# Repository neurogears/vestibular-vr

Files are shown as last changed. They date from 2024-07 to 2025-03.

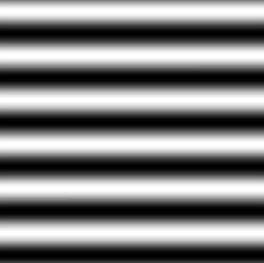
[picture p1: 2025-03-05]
Textures/horGrat.jpg

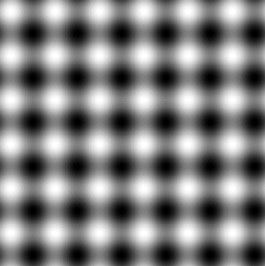
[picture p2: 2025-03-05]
Textures/plaid.jpg

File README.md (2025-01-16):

# vestibular-vr
Closed-loop VR setup for Rancz Lab

[Design Document](https://github.com/neurogears/vestibular-vr/blob/main/Design%20Documents/Vestibular%20VR%20Design%20Document.md)

### Acquisition Prerequisites

The following need to be installed on a fresh system in order to bootstrap the Bonsai environment correctly:

* Windows 10 or greater
* [Visual Studio Code](https://code.visualstudio.com/) (recommended for editing code scripts and git commits)
* [.NET 8.0 SDK](https://dotnet.microsoft.com/en-us/download/dotnet/8.0)
* [.NET Framework 4.7.2 Developer Pack](https://dotnet.microsoft.com/download/dotnet-framework/thank-you/net472-developer-pack-offline-installer) (required for intellisense when editing code scripts)
* [Git for Windows](https://gitforwindows.org/) (recommended for cloning and manipulating this repository)
* [Visual C++ Redistributable for Visual Studio 2012](https://www.microsoft.com/en-us/download/details.aspx?id=30679) (native dependency for OpenCV)
* [FTDI CDM Driver 2.12.28](https://www.ftdichip.com/Drivers/CDM/CDM21228_Setup.zip) (serial port drivers for HARP devices)
* [Spinnaker SDK 1.29.0.5](https://www.flir.co.uk/support/products/spinnaker-sdk/#Downloads) (device drivers for FLIR cameras, sign in required, look in the archived stable versions for 1.29.0.5)

### Setting up the Bonsai environment

To set up a Bonsai environment for running vestibular-vr, use the terminal to clone the repo into a local folder:

``` 
git clone https://github.com/neurogears/vestibular-vr.git
```

Now navigate into vestibular-vr/bonsai folder and run the `Setup.ps1` script (on Windows right-click > Run with powershell). Once all dependencies have been restored Bonsai can be launched in a local environment from the `.exe` in this folder.

### Session settings

Experiment parameters are based on a json schema (`schema.json` in the repo). Implementations of this schema are defined in `.yml` files provided by the user that are then loaded in the main Bonsai workflow to set up experiment parameters.

#### Working with schemas in Visual Studio Code
To create and edit schema implementations with full autcomplete and hinting, Visual Studio Code requires some extensions to be added:
* json (ZainChen.json)
* JSON Schema Validator (tberman.json-schema-validator)
* YAML (redhat.vscode-yaml)

#### Creating an experiment parameter file
To create an experiment parameter file based on the `schema`, create a new `.yml` file and add a reference to the `schema` at the top of the file

```
%YAML 1.1
---
# yaml-language-server: $schema=schema.json
```

The `schema` has two main groups of properties that define global experiment parameters, and block-specific parameters respectively, e.g.:

```
metadata:
  animalId: plimbo
  rootPath: D:/TrialLogicTestData/
  runGain: 0.0005

blocks: [
  &blockA
  {
    stimulus: {type: "grating"},
    totalRuntime: 20,
    runThreshold: 100,
    decayTimestep: 0.1,
    runThresholdDecay: -1,
    haltProbability: 0.5,
    haltProtocol: {
      minumumDelay: 0.1,
      randomDelay: 1.5,
      haltTime: 2,
      haltGain: 0
    }
  },
  &blockB
  {
    stimulus: {type: "cloud"},
    totalRuntime: 140,
    runThreshold: 200,
    decayTimestep: 0.1,
    runThresholdDecay: -1,
    haltProbability: 0.7,
    haltProtocol: {
      minumumDelay: 0.1,
      randomDelay: 0.5,
      haltTime: 0.5,
      haltGain: 0
    }
  },
  {<<: *blockA},
  {<<: *blockB}
]
```

The description of each parameter's effect on the Bonsai workflow, along with its type and default values are defined within `schema.json` itself. Note that where a parameter is not specifically set in the `.yml` the value will revert the default.

### Running an experiment
To run an experiment, run the Bonsai application from the local environment and open Main.bonsai. Use the property grid to select the desired experiment parameter `.yml` file.

### Python environment

The following need to be installed once on a fresh new system in order to analyze data:

 * [Visual Studio Code](https://code.visualstudio.com/) (recommended for editing code scripts and git commits)
 * A Conda distribution such as [Miniconda](https://docs.anaconda.com/free/miniconda/index.html)
 * [Python Extension for VS Code](https://marketplace.visualstudio.com/items?itemName=ms-python.python)
   * This extension needs to be made aware of the Conda installation. To do so, navigate to the extension settings. Under the section **Python: Conda Path**, enter the full path to the conda.bat executable. ([more info](https://stackoverflow.com/a/77615160/3312269).)
 * [Jupyter Extension for VS Code](https://marketplace.visualstudio.com/items?itemName=ms-toolsai.jupyter)

#### Create local Environment
1. Open the vestibular-vr folder in VS Code
2. `Ctrl+Shift+P` in VS Code > Python: Create Environment
   * Select Conda
   * Select Python 3.11 kernel
3. Ensure pip is upgraded:
 ```
 pip install --upgrade pip
 ```
4. From the terminal run `pip install -r requirements.txt`
5. Clone aeon_mecha into a separate directory 
 ```
 git clone https://github.com/SainsburyWellcomeCentre/aeon_mecha.git 
 ```
6. From the VS Code terminal, `cd` into the aeon_mecha directory and run:
 ```
 python -m pip install -e .
 ```

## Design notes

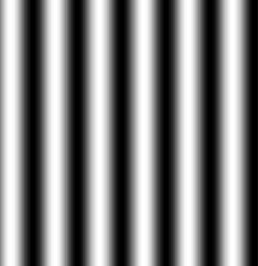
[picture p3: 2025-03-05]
Textures/vertGrat.jpg

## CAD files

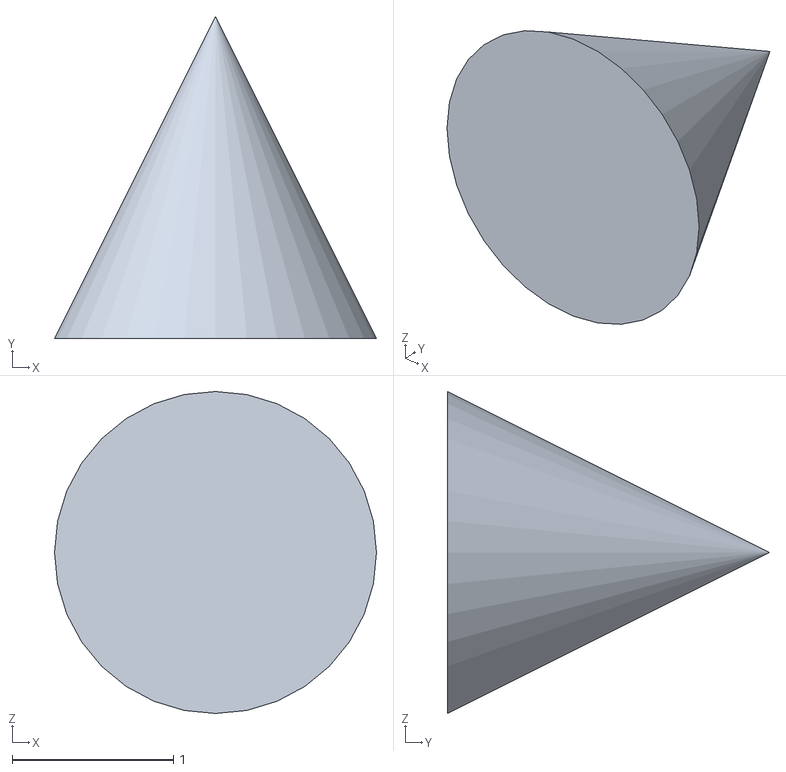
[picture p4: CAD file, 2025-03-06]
Models/cone.obj
2.00 x 2.00 x 2.00

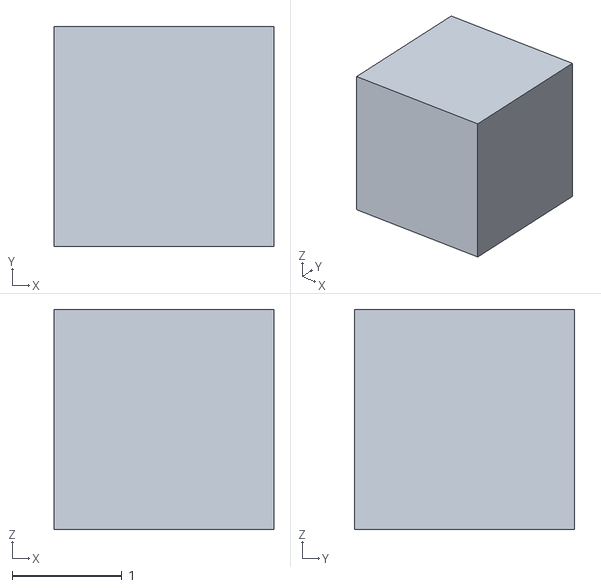
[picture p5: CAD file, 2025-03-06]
Models/box.obj
2.00 x 2.00 x 2.00

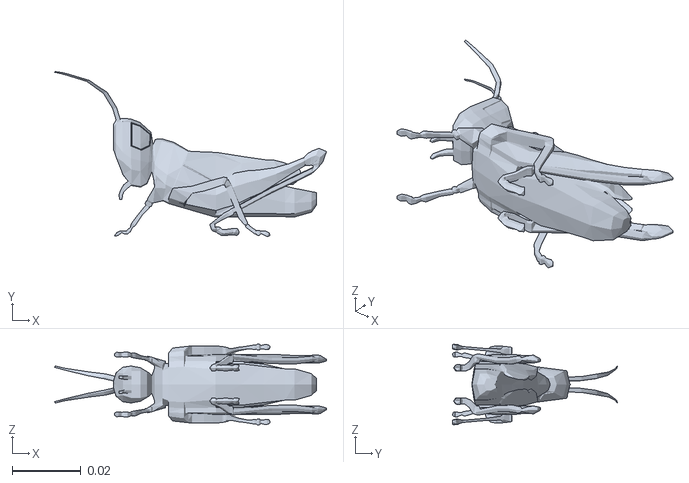
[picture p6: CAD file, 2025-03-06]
Models/cricket.obj
0.0788 x 0.0478 x 0.0234

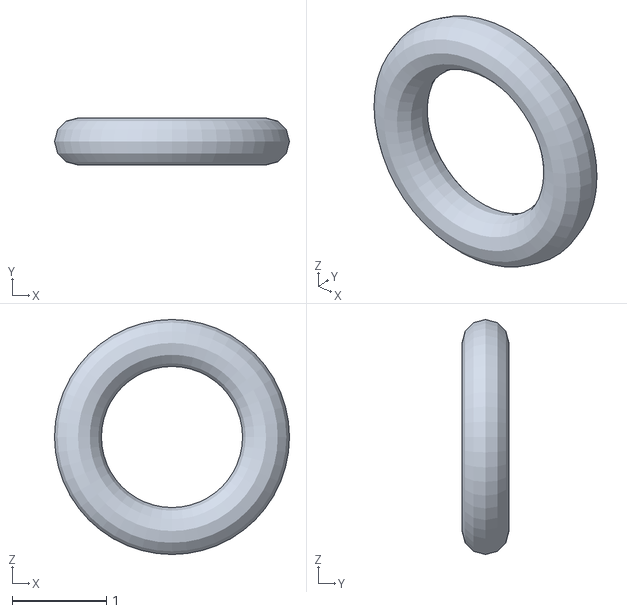
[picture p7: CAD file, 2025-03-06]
Models/torus.obj
2.50 x 0.5 x 2.50

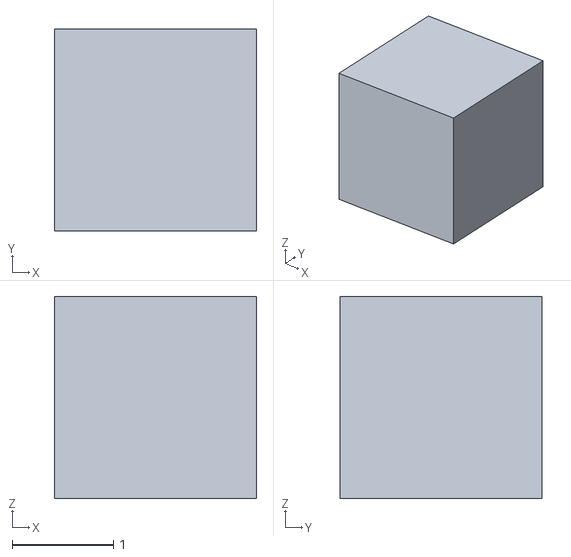
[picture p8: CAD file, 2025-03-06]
Models/cube.obj
2.00 x 2.00 x 2.00

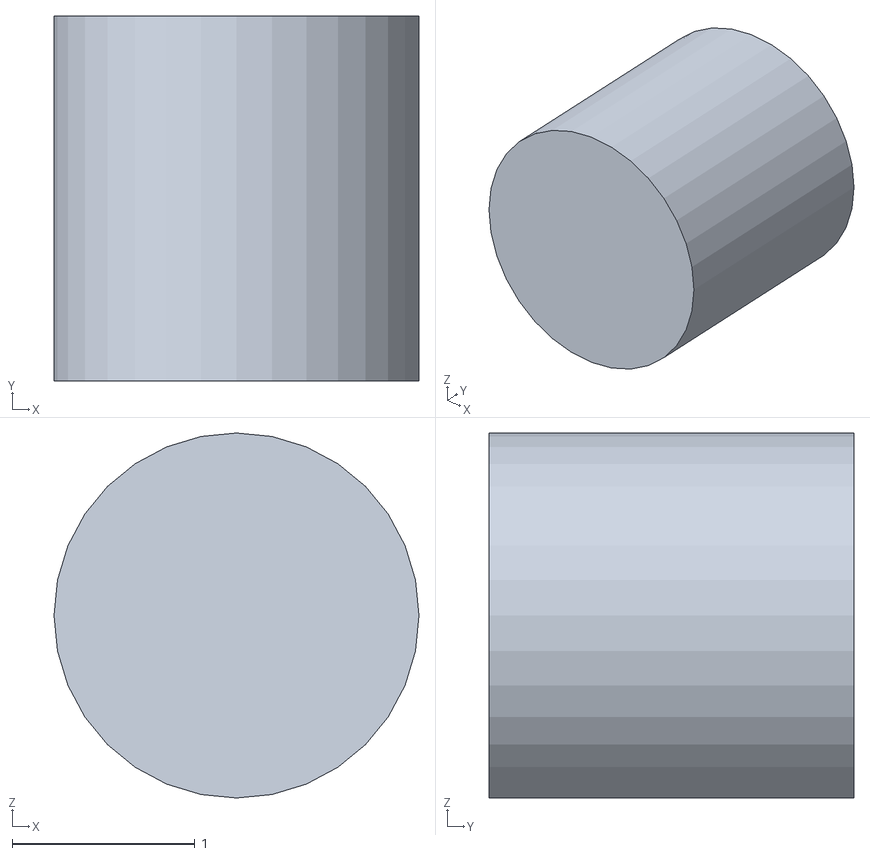
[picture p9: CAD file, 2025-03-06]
Models/cylinder.obj
2.00 x 2.00 x 2.00

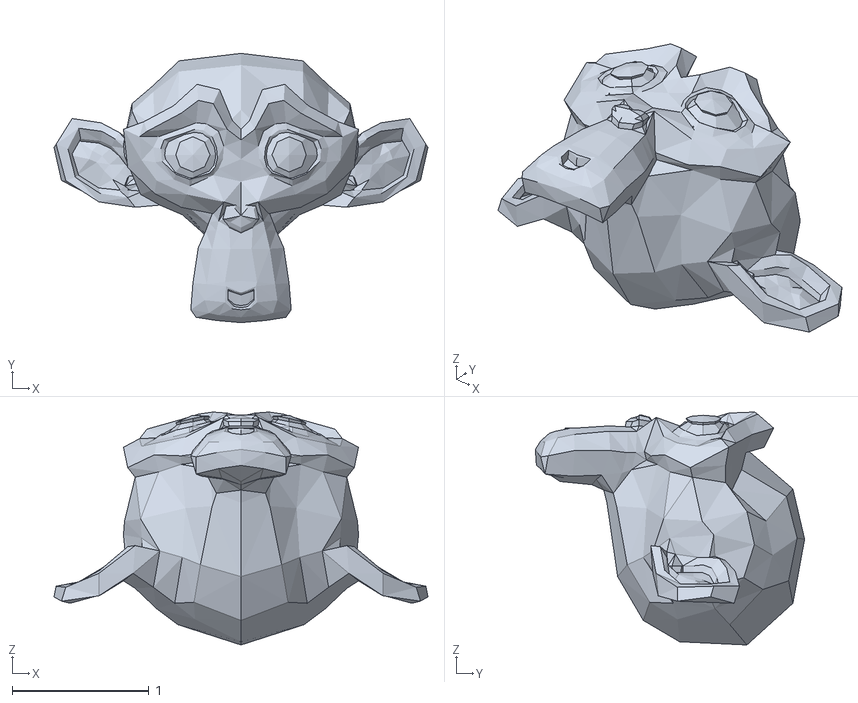
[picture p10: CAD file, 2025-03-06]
Models/suzanne.obj
2.73 x 1.97 x 1.70

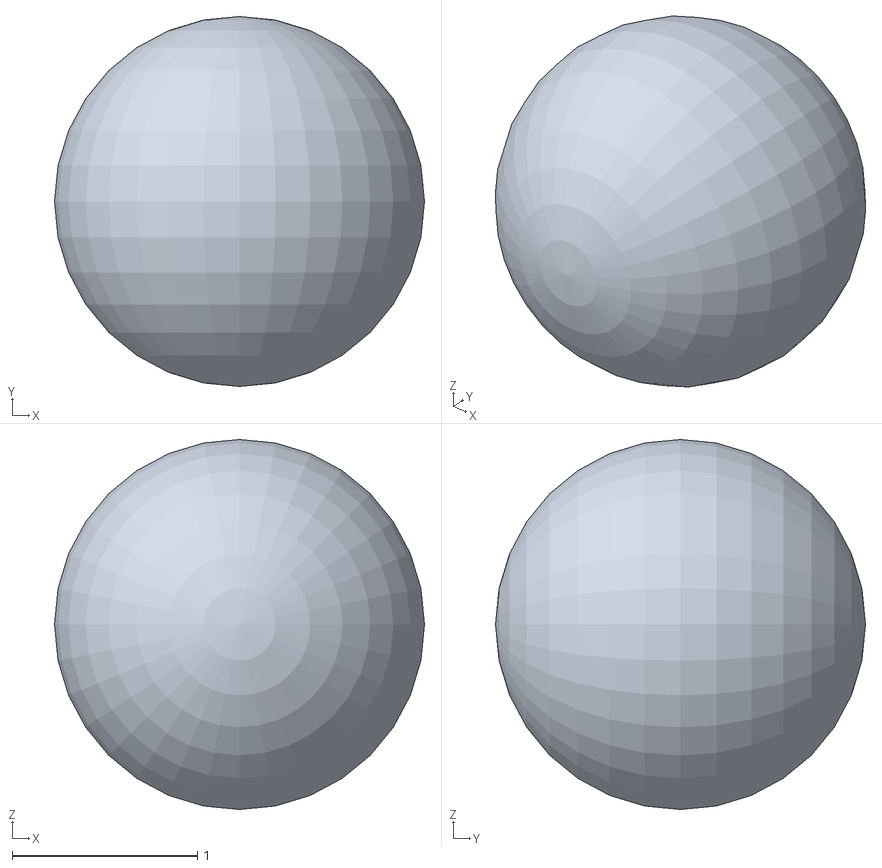
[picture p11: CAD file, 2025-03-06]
Models/sphere.obj
2.00 x 2.00 x 2.00

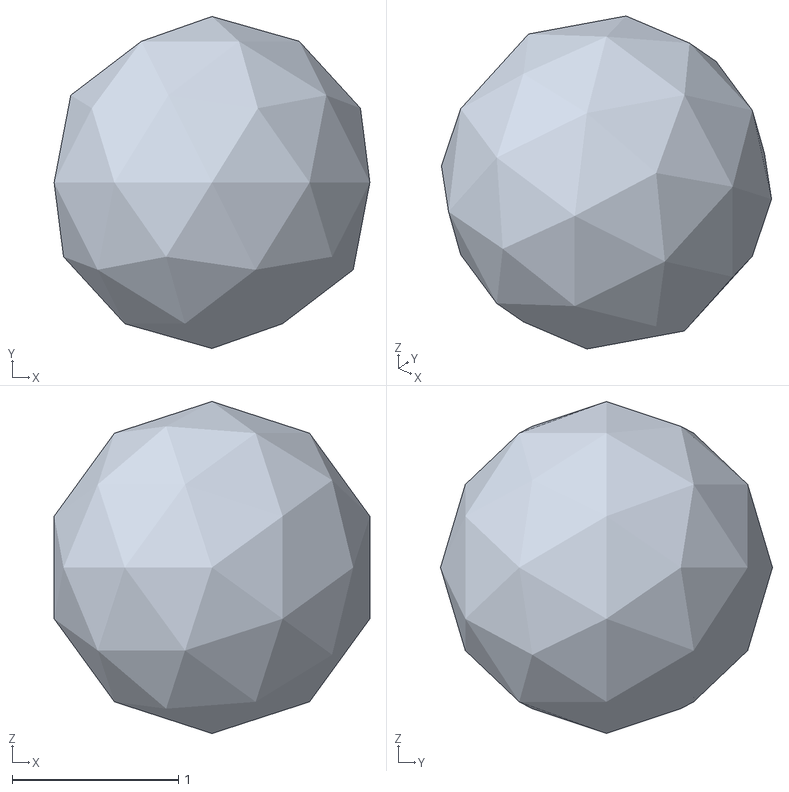
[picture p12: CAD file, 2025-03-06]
Models/icosphere.obj
1.90 x 2.00 x 2.00

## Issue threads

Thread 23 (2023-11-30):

### ISSUE TITLE
Video wall benchmarks

### ISSUE THREAD

**Issue by RoboDoig** [neurogears/vestibular-vr#23]
We need to test latency, jitter and synchronisation across screens with the matrox video wall.

- Thorlabs photodiodes
- Sampled through ONIX
- Standard closed-loop workflows for latency etc. timings
- NGR will provide workflow to be used onsite.

**Comment by ederancz** [comment]
Hey Andrew, can we close this or are you still analysing the data? Report the results here and then we can close it.

**Comment by RoboDoig** [comment]
Yes we should be able to soon, I'll upload the benchmark results here.

Do you have any kind of permanent cloud storage for lab data? Would be better to store raw data there rather than on the git repo.

**Comment by ederancz** [comment]
Good idea! 

We have a lab google drive, but I am not sure what is the easiest way for you to upload other than through the setup computer (Chrome should be logged in to ranczlab).

**Comment by RoboDoig** [comment]
Synchronisation between screens looks good, sub-millisecond

![image](https://github.com/neurogears/vestibular-vr/assets/11314305/0fb3f2a3-a3f0-4197-8a2b-1f748bbc637c)

**Comment by RoboDoig** [comment]
For latency and jitter, picture is a bit weirder. Hangs around 100ms latency. Jitter is mostly low but there are these higher latency events that pushes it up.

I would definitely expect these values to be lower, would be good to try this experiment again, also with a direct screen connection (not via Matrox) to compare.

![image](https://github.com/neurogears/vestibular-vr/assets/11314305/f0ffbe92-cf4f-452d-b734-81b19526971f)

**Comment by RoboDoig** [comment]
Poking around in the NVIDIA settings just now I also notice that there are a few options enabled that might slow down the display latency, let me know when available to repeat the test, I guess preferably after the rig has been moved.

**Comment by ederancz** [comment]
Cool, the setup won’t move before end of Jan, so Nora can set it up.-----------Sent from my phone, please excuse typos and brevity.On 22 Nov 2023, at 16:15, RoboDoig ***@***.***> wrote: 
Poking around in the NVIDIA settings just now I also notice that there are a few options enabled that might slow down the display latency, let me know when available to repeat the test, I guess preferably after the rig has been moved.

**Comment by RoboDoig** [comment]
Datasets for second round of benchmarks:

- Data2023_11_30_11_40_25 : Matrox only round-trip latency test
- Data2023_11_30_11_43_44: Matrox only screen-sync test

**Comment by RoboDoig** [comment]
Benchmarks with matrox only, NVIDIA ultra low latency mode, shader window focused on rig screens:

Screen_Sync:
![image](https://github.com/neurogears/vestibular-vr/assets/11314305/81edf5f5-a0cd-4a0f-84b4-765798e4cea6)

Round_Trip:
![image](https://github.com/neurogears/vestibular-vr/assets/11314305/873625fb-bb2d-49d1-ba2b-0f373cd7a06b)

I just noticed after doing this that the resolution set for the Matrox was at 7680x1080, at which the max refresh rate is 30Hz. Makes sense for the round-trip data where we are getting 1-2 frame delay at 30Hz. Will test at lower resolution with the full 60Hz, but will need someone to see what this physically looks like in the rig!

**Comment by RoboDoig** [comment]
Redid benchmarks with all monitors connected and latency jumped back up to ~100ms. @EleonoraAmbrad noticed that this was caused by Windows auto-selecting the Intel GPU as default when monitors are connected there. Fixed by forcing GPU choice to NVIDIA for the Bonsai exectuable in Windows graphics settings, Latency back down to 25-40ms.

**Comment by RoboDoig** [comment]
Added PR #34 which implements the benchmark workflows. I will merge the analysis scripts in a separate pull request, but closing this issue for now as desired latency / sync metrics achieved.

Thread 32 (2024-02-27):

### ISSUE TITLE
Implement full trial logic workflow

### ISSUE THREAD

**Issue by RoboDoig** [neurogears/vestibular-vr#32]
https://docs.google.com/document/d/1ItwPv-uNasmxrRA4Ncf8WAsi-0kBjkIqgoNdd-BLEN4/edit

**Comment by EleonoraAmbrad** [comment]
comments after meeting on the 7.11: trial logic works really well for our purposes, we would however like to control the time of the trials and not only the amount of halts / gain modulation episodes presented.

**Comment by RoboDoig** [comment]
Going back over this and I think I've been confusing myself with the concept of a 'trial' in this context.

Would it be fair to say that desired behaviour is to set for each block (e.g. mismatch block type 1)

- The total time the block should run for
- The minimum running threshold before a halt
- The probability of giving a halt after the threshold is reached
- The minimum delay before giving this halt if chosen, + a randomly sampled delay
- The total time the halt should be applied (contingent on the animal still running)
- The gain applied on each halt (e.g. 0 for total halt)

From re-reading the description it seems like there are not really discrete trials, just the process of checking running threshold and deciding whether to halt or not repeated throughout the block. I guess my question is whether any parameters need to change on each halt decision / presentation or whether these parameters are the same throughout the block (with the obvious exception of the random delay added to the minimum delay).

**Comment by EleonoraAmbrad** [comment]
yes, all you say here is correct, the parameters are set for each block. I think the word trial is a bit misleading, as each block will contain the set of parameters you listed and nothing should change except the random delay after the minimal delay

**Comment by RoboDoig** [comment]
Ok that's great thanks! I'm much clearer on this now.

**Comment by EleonoraAmbrad** [comment]
NPX data visualiser: following the meeting on the 2.2.24, we agreed with Gonçalo that the shader visualiser should be calibrated to our data.

In the Debug workflow, one of the NPX channels was streamed to the AnalogIO on the ONIX, then displayed on an oscilloscope. This works well on this workflow, but not in the "Insertion Workflow" that is used to record data at the moment (data displayed by the oscilloscope does not match voltage trace recorded by ONIX). 

It would be great if the changes applied in the MinimalONIXDebug workflow were replicated in the Insertion Workflow

**Comment by RoboDoig** [comment]
> NPX data visualiser: following the meeting on the 2.2.24, we agreed with Gonçalo that the shader visualiser should be calibrated to our data.
> 
> In the Debug workflow, one of the NPX channels was streamed to the AnalogIO on the ONIX, then displayed on an oscilloscope. This works well on this workflow, but not in the "Insertion Workflow" that is used to record data at the moment (data displayed by the oscilloscope does not match voltage trace recorded by ONIX).
> 
> It would be great if the changes applied in the MinimalONIXDebug workflow were replicated in the Insertion Workflow

This s added with PR #40

**Comment by RoboDoig** [comment]
Closing this issue with PR #44

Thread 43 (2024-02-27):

### ISSUE TITLE
ONIX failure after NewScale runtime error

### ISSUE THREAD

**Issue by RoboDoig** [neurogears/vestibular-vr#43]
The purpose of this issue for now is to keep a record of an observed bug.

Workflows containing the NstDevice operator can produce a runtime error if no NewScale device is connected. It seems that this error also interferes with initialisation of ONIX components by Bonsai and causes the ONIX device to end up in a weird state which crashes when the workflow is reset. The hardware can be reset by running the oni-repl program.

Can't really do anything about this until the ONIX Bonsai interface is updated. For now need to make sure NewScale is connected before starting any workflows with ONIX components.

**Comment by EleonoraAmbrad** [comment]
good idea to open this issue! 

could you remind me whether the liboni repo that you used was the one we had backed up from the previous computer or if you had to build the solution on visual code starting from the newly downloaded repo? I think I missed that yesterday. Thanks!

**Comment by RoboDoig** [comment]
In the end I did not use the backed up liboni folder. I cloned the repo and built the oni-repl.exe from source.

Closing this issue in favor of #45

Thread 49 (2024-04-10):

### ISSUE TITLE
Workflow specifications

### ISSUE THREAD

**Issue by RoboDoig** [neurogears/vestibular-vr#49]
@EleonoraAmbrad @ederancz Please use this issue to upload detailed specs for final experiment workflows.

**Comment by EleonoraAmbrad** [comment]
when using the workflow "TrialLogicTest" I ran into two behavior I did not understand:
- does the workflow stop after a few number of halts have been reached no matter the block length? This happened when setting halt probability to >0. Also, when this happens, the next commands are ignored (i.e. the blocks do not repeat even if specified in the json file)
- I am not sure the block gain modifier in the json file is working, the global gain seems to be the only one taken into account?

**Comment by RoboDoig** [comment]
> when using the workflow "TrialLogicTest" I ran into two behavior I did not understand:
> 
>     * does the workflow stop after a few number of halts have been reached no matter the block length? This happened when setting halt probability to >0. Also, when this happens, the next commands are ignored (i.e. the blocks do not repeat even if specified in the json file)
> 
>     * I am not sure the block gain modifier in the json file is working, the global gain seems to be the only one taken into account?

The workflow should not stop after a certain number of halts, the only thing that should stop the block is the block length timer if I recall correctly. Is it always stopping after a certain number of halts?
The block gain modifier is definitely implemented, it should multiply the global gain

**Comment by RoboDoig** [comment]
Some comments on the workflow specification that I'd like to clarify:

- "The rotation of the VR should be coupled to the motor movement..." - as I understand it we should therefore couple VR movement to the rotary encoder?
- Will playback just be playback of the visual stimulus, or the motor movement as well?
- "Motion cloud - link to python configuration script": To be clear, at the moment the motion clouds are generated via a python script as static texture sequences and loaded as a texture movie in Bonsai. Does this need to change? I think we had agreed that it was better to pre-generate the texture sequences rather than having them load dynamically.
- Algorithm 2 is greyed out in the experimental design document, is it required?

**Comment by EleonoraAmbrad** [comment]
> > when using the workflow "TrialLogicTest" I ran into two behavior I did not understand:
> > ```
> > * does the workflow stop after a few number of halts have been reached no matter the block length? This happened when setting halt probability to >0. Also, when this happens, the next commands are ignored (i.e. the blocks do not repeat even if specified in the json file)
> > 
> > * I am not sure the block gain modifier in the json file is working, the global gain seems to be the only one taken into account?
> > ```
> 
> The workflow should not stop after a certain number of halts, the only thing that should stop the block is the block length timer if I recall correctly. Is it always stopping after a certain number of halts? The block gain modifier is definitely implemented, it should multiply the global gain

I had the impression that the workflow stopped too early after setting halt probability to >0. For sure, the blocks that should come after do not start when this happens

**Comment by RoboDoig** [comment]
Could you send me an example SessionSettings file that produces this behavior? I will investigate

**Comment by EleonoraAmbrad** [comment]
> Some comments on the workflow specification that I'd like to clarify:
> 
> * "The rotation of the VR should be coupled to the motor movement..." - as I understand it we should therefore couple VR movement to the rotary encoder?

yes, that is what we thought. It would be analogous to reading out the PMW and translating it to VR motion, but for the rotation. 
> * Will playback just be playback of the visual stimulus, or the motor movement as well?

Just the VR. We would like to be able to control motor movement "freely" as well,  but that is a separate issue

> * "Motion cloud - link to python configuration script": To be clear, at the moment the motion clouds are generated via a python script as static texture sequences and loaded as a texture movie in Bonsai. Does this need to change? I think we had agreed that it was better to pre-generate the texture sequences rather than having them load dynamically.

no, this does not need to change, sorry, I formulated it wrong here. The way it'S working now is good!
> * Algorithm 2 is greyed out in the experimental design document, is it required?

no, it was a suggestion on how to implement the workflow, but does not necessarily need implementation
> 
> Finally, I think it would be ideal if we could combine both the linear flow and rotating drum environments into a single workflow. We could control the experiment type with block definitions as we do now.

this would be great, I think it would work well. Just to be clear, we would also like to display rotating visual stimuli passively and rotate the motor at a certain speed and gain (this should be mentioned in the new pdf, but I wanted to make sure it's clear again :D )

thanks a lot!

**Comment by RoboDoig** [comment]
Thanks @EleonoraAmbrad that makes things much clearer. Also as you say, the playback condition needs to still be implemented for both the linear and drum environments.

There is one distinction I still need to clarify: "It would be analogous to reading out the PMW and translating it to VR motion, but for the rotation." - 
We can link the VR movement to the PWM that is sent to the motor controller but ultimately this is calculated directly from the flow sensor reading. The alternative is that we read out the rotary encoder signal that is produced **as a result** of the motor movement and use that to drive the VR motion.

**Comment by RoboDoig** [comment]
I also have a question about the relationship between the four types of block. We have:

- Closed-loop
- Open-loop
- Mismatch
- Playback

As I understand it there are really only two conditions - closed-loop and open-loop. A mismatch block is always subset of a closed-loop block (where halt probaility > 0). A playback block is always a subset of an open-loop block. Is that correct?

**Comment by RoboDoig** [comment]
I think in fact all these conditions can be reduced to a single block type with different gain settings:

Linear, closed-loop:
- flow-->vr gain > 0 (or < 0)
- flow-->motor gain = 0
- rotary-->vr gain = 0
- playback-->vr gain = 0
- (+/-) mismatch parameters

Linear, playback:
- flow-->vr gain = 0
- flow-->motor gain = 0
- rotary-->vr gain = 0
- playback-->vr gain >0 (or <0)
- (+/-) mismatch parameters

Drum, closed-loop:
- flow-->vr gain = 0
- flow-->motor gain = >0 (or <0)
- rotary-->vr gain = >0 (or <0)
- playback-->vr gain = 0
- (+/-) mismatch parameters

Drum, playback:
- flow-->vr gain = 0
- flow-->motor gain = 0
- rotary-->vr gain = 0
- playback-->vr gain = >0 (or <0)
- (+/-) mismatch parameters

**Comment by RoboDoig** [comment]
Another couple of things to clarify:

"Rotation probability: probability of the played back or generated flow stopping at
each given time" - this suggests that there should be defined times for halting playback? Is this true or is it just with the randomisation parameters as implemented now?

**Comment by EleonoraAmbrad** [comment]
> I think in fact all these conditions can be reduced to a single block type with different gain settings:
> 
> Linear, closed-loop:
> 
> * flow-->vr gain > 0 (or < 0)
> * flow-->motor gain = 0
> * rotary-->vr gain = 0
> * playback-->vr gain = 0
> * (+/-) mismatch parameters
> 
> Linear, playback:
> 
> * flow-->vr gain = 0
> * flow-->motor gain = 0
> * rotary-->vr gain = 0
> * playback-->vr gain >0 (or <0)
> * (+/-) mismatch parameters
> 
> Drum, closed-loop:
> 
> * flow-->vr gain = 0
> * flow-->motor gain = >0 (or <0)
> * rotary-->vr gain = >0 (or <0)
> * playback-->vr gain = 0
> * (+/-) mismatch parameters
> 
> Drum, playback:
> 
> * flow-->vr gain = 0
> * flow-->motor gain = 0
> * rotary-->vr gain = 0
> * playback-->vr gain = >0 (or <0)
> * (+/-) mismatch parameters
> 
> This way you are also not as limited in choosing 1 of 4 block types. You can still construct the original types but also do things in between (e.g. have a drum playback block that also has some closed-loop rotary motion).

This looks really efficient and straightforward, I like it a lot. I can't see anything wrong with doing it this way. Basically one will control each component at the time.
How does one deal with length of the "block" though in this case? An extra parameter?

**Comment by EleonoraAmbrad** [comment]
> Thanks @EleonoraAmbrad that makes things much clearer. Also as you say, the playback condition needs to still be implemented for both the linear and drum environments.
> 
> There is one distinction I still need to clarify: "It would be analogous to reading out the PMW and translating it to VR motion, but for the rotation." - We can link the VR movement to the PWM that is sent to the motor controller but ultimately this is calculated directly from the flow sensor reading. The alternative is that we read out the rotary encoder signal that is produced **as a result** of the motor movement and use that to drive the VR motion.

This makes sense, it would be also more accurate I guess

**Comment by EleonoraAmbrad** [comment]
> Another thing to clarify:
> 
> "Rotation probability: probability of the played back or generated flow stopping at each given time" - this suggests that there should be defined times for halting playback? Is this true or is it just with the randomisation parameters as implemented now?

This I don't know about yet. Since we haven't finally implemented the playback I'm not sure anymore which strategy we had decided to go with (playback in VR of another mouses movement based on flow sensor or random generation of visual stimuli?) Both strategies are working I'd say, as long as the times when the halts occur are logged. I'm sorry if I'm not getting your question :/

**Comment by RoboDoig** [comment]
Re: playback - for now I am going to implement this with analog input as the source of the playback signal. This can be coupled to visual flow or motor movement in any way you want with the gain settings. Or you can change the source to be something other than analog input.

**Comment by RoboDoig** [comment]
Closing this issue as implemented and tested.

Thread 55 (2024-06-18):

### ISSUE TITLE
Provide example data files as reference

### ISSUE THREAD

**Issue by RoboDoig** [neurogears/vestibular-vr#55]
For working on some of the open issues (#53 #54) it would be beneficial to have some example logged data as a reference (in particular the HARP streams).

@EleonoraAmbrad could you provide some data from a run of the Main.bonsai trial logic workflow? This will be particularly useful as a reference for Filipe when implementing direct H1 --> H2 motor control.

**Comment by EleonoraAmbrad** [comment]
files sent via email (link to google drive folder)

**Comment by EleonoraAmbrad** [comment]
@RoboDoig asking for advice: I am looking at the data produced by the video writer node, the csv file VideoData1_1904-01-01T00-00-00.csv 
 It looks like there is some substantial frame loss over time? or am I interpreting things wrong? Do we need to reduce frame rate?

**Comment by EleonoraAmbrad** [comment]
> Hi @EleonoraAmbrad, what in the csv file is suggesting this? Is it just the number of frames or something in the frame timestamps?

Value.ChunkData.FrameID: these values are consecutive until a certain point (until frame 40), but then they are not anymore. Seems like every second frame is dropped after this, but it's not consistent (sometimes more or less than this)

**Comment by RoboDoig** [comment]
Also doesn't seem to be the case in the last dataset I downloaded from the google drive (2024-05-10T14-22-41). Are both cameras set at the same frame rate / exposure time?

**Comment by EleonoraAmbrad** [comment]
> Also doesn't seem to be the case in the last dataset I downloaded from the google drive (2024-05-10T14-22-41). Are both cameras set at the same frame rate / exposure time?

you're right, maybe there was a mistake then. Or maybe it's a problem when keeping the spin view software open? I need to do that to set the gain at the moment.

**Comment by EleonoraAmbrad** [comment]
on that specific file not, but if you look at VideoData1_1904-01-03T23-00-00.csv it happens there as well. 

Yeah the cameras have the same frame rate and exp time, but in general this shouldn't be a problem right? (they are on different triggers now). One thing that comes to mind is that I have to keep SpinView software open to set the gain, could that be an issue?

**Comment by RoboDoig** [comment]
> on that specific file not, but if you look at VideoData1_1904-01-03T23-00-00.csv it happens there as well.

On which dataset?

> Yeah the cameras have the same frame rate and exp time, but in general this shouldn't be a problem right? (they are on different triggers now). One thing that comes to mind is that I have to keep SpinView software open to set the gain, could that be an issue?

Keeping the software open shouldn't be an issue. 

Can you reproduce the missing frames reliably? If so what happens if you swap the trigger lines for the cameras?

**Comment by EleonoraAmbrad** [comment]
> > on that specific file not, but if you look at VideoData1_1904-01-03T23-00-00.csv it happens there as well.
> 
> On which dataset?
> 
> > Yeah the cameras have the same frame rate and exp time, but in general this shouldn't be a problem right? (they are on different triggers now). One thing that comes to mind is that I have to keep SpinView software open to set the gain, could that be an issue?
> 
> Keeping the software open shouldn't be an issue.
> 
> Can you reproduce the missing frames reliably? If so what happens if you swap the trigger lines for the cameras?

sorry, on the 2024-05-10T14-20-05. I don't think the loss can be reliably reproduced because these recordings were all done on the same day with the same settings, I only changed sampling rate and exp time. I am not sure whether this reliably happens with increasing sampling rate, for example, or when setting a sample rate that is too high for what the exposure time allows. In any case it's strange that this happens only for 1 camera when both had the same sampling rate and exposure time. I will test this more systematically, swap the triggers and come back to you asap

**Comment by EleonoraAmbrad** [comment]
I uploaded some more files in the drive. these files were acquired with harp clock sync device (received this week) connected to h2, and h2 sending clock signal to h1. 

in the last recorded files I see frame drops in both cameras even if I change the sampling rate and exposure time and swap the triggers. 

another interesting behavior is that sometimes when I stop the workflow and restart it, the cameras are already triggered. stopping the workflow and restarting it solves the issue. not a big deal I guess, unless it's indicative of underlying trigger issues?

**Comment by RoboDoig** [comment]
Hi @EleonoraAmbrad I'm closing this issue as the original problem is resolved. Could you create a new issue for the camera trigger observation if it's still a problem?

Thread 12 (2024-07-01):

### ISSUE TITLE
Bonsai workflows 

### ISSUE THREAD

**Issue by ederancz** [neurogears/vestibular-vr#12]
Hi @RoboDoig. There are 2 example workflows below. 

In general, all workflows should have the following: 
1. Some sort of lab-book / metadata (time/date, animal ID, various experiment parameters e.g. gain in open loop).
2. Save processed optical sensor signals as styrofoam ball position. If using 1 optical sensor, then cumulative forward travel of the animal (say in cm) and rotation (0-360 degrees). This will of course need to be calibrated. In the future, we may want to use 2 sensors and average them for the rotation measure. 
3. Trigger and save from 1 camera. In the future, online deepLabCut analysis would be sweet and perhaps only record pupil diameter and position. 
4. A homing function. Currently using a hall-effect sensor and a magnet and rotate the platform until we activate it. 

**Workflow 1. Closed loop** 
Inputs: Target position, speed, max acceleration 
Outputs: motor command, styrofoam ball position, video 
For the future: follow arbitrary waveform as a positional command 

**Workflow 2. Open loop** 
Inputs: optical sensor signal, gain (between optical sensor and motor movement)  
Outputs: motor command, styrofoam ball position, video

Regarding motor command, we should discuss motion control fairly soon. It is a big field, and I am not well-versed in it.

**Comment by RoboDoig** [comment]
Can I assume that this issue is superseded by #49 ? Is there anything mentioned in this issue that is missing from the more recent workflow specs?

**Comment by EleonoraAmbrad** [comment]
yes, this issue can be closed!

> Can I assume that this issue is superseded by #49 ? Is there anything mentioned in this issue that is missing from the more recent workflow specs?

I think we can close this issue, thank you !

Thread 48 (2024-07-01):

### ISSUE TITLE
Implement synchronisation between HARP and ONIX

### ISSUE THREAD

**Issue by RoboDoig** [neurogears/vestibular-vr#48]
Ideally, HARP interface of ONIX breakout will be used as a master clock for H1/H2.

Implement photodiode synchronisation on screens (flickering square to synchronise draw calls).

Use WithLatestTimestamp approach to log state changes in block state machine.

**Comment by EleonoraAmbrad** [comment]
we have a jack "stereo" cable that we can use for the synchronisation as suggested above. 

According to the design files, the harp interface signal should be split between H1 and H2, is this correct? If so, should I strip the cable and use the screw terminals on H1 and H2? 
![SignalRoutingDesign](https://github.com/neurogears/vestibular-vr/assets/143619542/50209ff6-1a8f-4c80-a445-6bba61ee1231)
![photo_2024-04-16 14 27 59](https://github.com/neurogears/vestibular-vr/assets/143619542/ac11d373-d42b-47cc-b2f1-f10b813ec53e)

**Comment by RoboDoig** [comment]
There are a couple of ways to do it, as you say you can take a stereo 3.5mm cable and have one end in H2, then bare wire in the screw terminals for H1. 

You can also get the HARP synchronizer (https://www.cf-hw.org/open-source-tools/electronic-devices/clock-synchronizer) which can act as the master clock source and has multiple output channels that you can send to H1, H2 and ONIX

**Comment by EleonoraAmbrad** [comment]
> There are a couple of ways to do it, as you say you can take a stereo 3.5mm cable and have one end in H2, then bare wire in the screw terminals for H1.
> if we were to go with this solution, how would the ONIX receive the sync signals? i.e. which connection on the breakout board should be setup?

**Comment by RoboDoig** [comment]
I don't think the ONIX can generate a HARP clock, it would rather be H2 generating the master clock and then H1 and ONIX receiving that clock. But yes, the cable would have to be split out from H2 to go to H1 and ONIX, e.g. with a 3.5mm splitter.

https://www.amazon.co.uk/PENCILUPNOSE%C2%A9-HEADPHONE-SPLITTER-EXTENSION-MOTOROLA-BLACK/dp/B079GBP6CV/ref=asc_df_B079GBP6CV/?tag=googshopuk-21&linkCode=df0&hvadid=375419269630&hvpos=&hvnetw=g&hvrand=17305413413427148390&hvpone=&hvptwo=&hvqmt=&hvdev=c&hvdvcmdl=&hvlocint=&hvlocphy=9046001&hvtargid=pla-1013889856952&psc=1&mcid=d37b23cc42a13f0186f1f5c3478351d8&tag=&ref=&adgrpid=85278568708&hvpone=&hvptwo=&hvadid=375419269630&hvpos=&hvnetw=g&hvrand=17305413413427148390&hvqmt=&hvdev=c&hvdvcmdl=&hvlocint=&hvlocphy=9046001&hvtargid=pla-1013889856952

**Comment by EleonoraAmbrad** [comment]
update after meeting with @RoboDoig : signal should not be split between H1 and ONIX from H2, so we will instead send a randomized synchronisation ANALOG output signal to H2 and ONIX. Analog output will be generated in bonsai. 

Ideally, in the future we should rely on https://www.cf-hw.org/open-source-tools/electronic-devices/clock-synchronizer to split clock output to H2 and ONIX, especially because H2 analog input may be needed for playback signal.

**Comment by RoboDoig** [comment]
After last week's discussion: to synchronize everything correctly it will definitely be necessary to use a clock-synchronizer. The H2 analog input is occupied by the hall sensor so it can't be used as a synchronisation signal. Solution will be to have the clock-sync connected to H2 and ONIX. H2 will then pass its clock signal to H1 via the rotary joint.

**Comment by EleonoraAmbrad** [comment]
Order for the clock synchroniser will be placed this week, lead time should be 2 days.

**Comment by EleonoraAmbrad** [comment]
quick question: the HARP sync signal sent to ONIX will go in the dedicated hair sync 3.5 mm connection? this means that we would need a cable with two male audio connectors (one for the jack on clock sync and one for the ONIX?)

**Comment by ederancz** [comment]
Implemented now. There is now way to test it (would need two identical HARP devices with the same inputs), but we have no reason to believe it is not working.

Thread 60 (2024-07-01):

### ISSUE TITLE
Array names in device schema for postprocessing

### ISSUE THREAD

**Issue by RoboDoig** [neurogears/vestibular-vr#60]
Currently, the device schema for H1 does not have names for array columns in e.g. OpticalTrackingRead. This causes an issue with postprocessing analysis as harp-python cannot parse the array data without modifications.

To fix this on the postprocessing branch, the device schema should use named columns for array data.

**Comment by RoboDoig** [comment]
@EleonoraAmbrad @ikharitonov I've made the changes to the analysis code we talked about in the meeting today. Try out the `reader-proto` branch for an example

**Comment by ikharitonov** [comment]
@RoboDoig thanks! OpticalTrackingRead works, along with Cam0Event, Cam1Event and StartAndStop, but the rest are failing with "ValueError: No objects to concatenate". Also we found the YAML file for H2 (https://github.com/harp-tech/device.vestibularH2/blob/main/Firmware/VestibularVrH2/device.yml), but most registers there are also failing to be read

**Comment by RoboDoig** [comment]
That might be because no events were logged for the other registers, for example if I look in the example harp data folder I have - I see events only for 32, 33, 38, 46 (Cam0Event, Cam1Event, StartAndStop, OpticalTrackingRead).

Could you double check whether reading a register fails even when there is definitely binary data available for it?

**Comment by ikharitonov** [comment]
You are right sorry, we realised after posting, readable registers match with available binaries

**Comment by RoboDoig** [comment]
Can you confirm it's working now? If so I will make a PR and close this issue.

**Comment by ederancz** [comment]
Working fine, device.yml files need updating (or confirming) for current firmware versions for H1 and H2, created issues at harp repos.

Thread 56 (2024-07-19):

### ISSUE TITLE
synchronisation of bonsai H1 and H2 events with photometery system

### ISSUE THREAD

**Issue by EleonoraAmbrad** [neurogears/vestibular-vr#56]
we would like to implement synchronisation between the data acquired via H1 and H2 and a photometry setup when using the Main experiment workflow.

https://www.rwdstco.com/product-item/dual-color-fiber-photometry-system/?_gl=1*r9q6pp*_up*MQ..*_ga*MTc5NzE1ODA1MS4xNzE1Nzc1MzE0*_ga_2P56W6VQP2*MTcxNTc3NTMxMy4xLjEuMTcxNTc3NTMzMi4wLjAuMA..&gclid=CjwKCAjwupGyBhBBEiwA0UcqaBYzOFXJ-Fceqbl8VPrT6yq4bXvHe9BTilrouICISsTUCkpdJtkFxxoCX_MQAvD_BwE (link to setup)

at the moment, a digital output of the ONIX is used to send a continuous 5V pulse to the RWD input to signal visual stimulus onset in a different workflow, but this approach is not optimal.

additionally, synchronisation with Harp devices would be required to align calcium imaging data to pupil tracking cameras and flow sensor data. Help with this would be greatly appreciated once we set up clock sync on H1 and H2!

**Comment by ederancz** [comment]
Requirements: 

1. Bonsai to generate pseudorandom TTL pulse and send it out of ONIX digital out. These need to be logged with HARP timestamps. 
2. This has to be implemented in a duplicate insertion.workflow to contain an ONI node.

**Comment by RoboDoig** [comment]
This all makes sense, just wondering about point 2. though - is there an advantage to using a premade csv file for the ON/OFF states vs. generating them online and logging the order for each experiment?

**Comment by EleonoraAmbrad** [comment]
we were maybe thinking it's easier, but if not then generating online is also an option of course

**Comment by RoboDoig** [comment]
My thinking is along these lines:

If you have a predetermined ON/OFF timing sequence loaded from .csv you have to load it into the workflow at runtime, which is fine. There may be a situation where you generate a few different .csv files for this, and you need to log somewhere which one you have used in Bonsai. This can be as simple as logging the name of the .csv file used, or you could 'relog' the entire file along with everything else to be 100% sure which sequence you used for synchronisation.

I can imagine a tricky situation happening somewhere down the line where you have been using a sequence file ('sequence.csv') and then at some point it's decided to change the sequence for some reason. The name of the logged file is the same but the sequence is different leading to potential confusion in later analysis.

This needs to be avoided, so to be safe we need to log the entire sequence anyway along with the corresponding HARP timestamps. Since this all needs to be logged anyway, to me it makes sense to just generate the sequence online in Bonsai. Unless there is some advantage of a predetermined sequence that I'm missing. Additionally, you can effectively have a predetermined sequence while generating it online by setting a seed for your random generator in the workflow.

**Comment by RoboDoig** [comment]
I've implemented a photometry sync signal in the photometry-sync branch. The signal is set on digital output 0 of the ONIX. To fully test we need to route that signal to the photometry setup and also reroute it to a digital input on the ONIX so we can ensure that it's being logged correctly with HARP timestamps.

**Comment by EleonoraAmbrad** [comment]
the photometry sync signal works well! as discussed, we would need the signal to stop right after the trial logic is over, to signal that the experiment is also finished (at the moment the TTL is still ON after the trial logic ends).

**Comment by RoboDoig** [comment]
I branched the digitalOUT from pin 0 to the A1 pin on ONIX

**Comment by EleonoraAmbrad** [comment]
i branched out the digitalO0 to A1 on onix

**Comment by RoboDoig** [comment]
I would suggest branching instead to a digital input line, the reason being that each digital input event is HARP timestamped, whereas the analog data is acquired and timestamped in chunks. Practically this might not make that much difference to your synchronisation precision, but if you ever e.g. change the chunk size of the analog inputs it might have an effect.

**Comment by RoboDoig** [comment]
Depending on the ONIX board you have, there is an issue with the HARP clock physical input. For certain versions of the ONIX board (I think this is an issue with 1.5B) the HARP clock jack actually sends a HARP clock signal OUT rather than receives the clock from an external device. Our design for the system relies on the ONIX board receiving the HARP clock from an external device.

My understanding is that they originally intended the ONIX boards to act as master HARP clocks sending clock signals out to other devices and then changed the direction in later versions.

To fix this at a hardware level, there is an adapter developed at OEPS that allows the ONIX board to receive HARP clock signals as input. I am asking Filipe how to obtain this. For now since the digital inputs of the ONIX are paired with HARP timestamps in the Bonsai workflow I suggest that we add another digital output --> digital input loopback in ONIX that can be used to synchronise HARP with the ONIX.

Potential solutions summarised:

1. Get a HARP clock adapter for ONIX from Filipe
2. Create another DO --> DI loopback in ONIX so that we can use DI events to synchronise with HARP
3. Depending on whether the photometry system is capable of recording at a high enough sampling rate, just speed up the photometry sync signal (rather than going for option 2)
4. Investigate whether the clock synchroniser device can be used as a repeater for the ONIX clock output.

Also please double check what version of the ONIX breakout board you have so we can confirm this is an issue that needs to be addressed.

**Comment by EleonoraAmbrad** [comment]
can confirm hat the board is the 1.5 B (beta). 

I am currently setting up the DO1->DI1 connection for the synchronistation and the DO0->DI0 for the photometry sync signal.
We cannot use the photometry sync signal for both purposes (option 3) because the analog IN is going to be sampled at rates between 10 and 30 Hz., so we should either revert the direction of the clock synchroniser device or use the digital loop while we wait for the adaptor.

**Comment by EleonoraAmbrad** [comment]
done

**Comment by RoboDoig** [comment]
Re: the sync signal stopping after trial logic is done. I assume by this you mean you want the sync signal to stop only after all blocks are done?

I'm not sure I understand why this is desirable as it creates some ambiguity when used as a trial logic signal as well as a photometry sync signal.

Consider the last block of the sequence, as the sync signal is switching high to low with a random time interval, if the last sync signal is a switch to low, followed by setting again at low for the end of the block sequence you would not know when the block had actually ended.

**Comment by RoboDoig** [comment]
Should be fixed by #64, pending testing.

**Comment by RoboDoig** [comment]
Confirmed working after testing.

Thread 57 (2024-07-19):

### ISSUE TITLE
Screen sync quad

### ISSUE THREAD

**Issue by RoboDoig** [neurogears/vestibular-vr#57]
Need to implement a method of synchronising screen updates, as well as visual halts with everything else (HARP ONIX)

Proposed solution is to use a flickering quad somewhere in the corner of the screen with a photodiode recording. The parameters of this flicker (e.g. color) should be changed during halt periods so we can recover both the screen update as well as the timing of each halt.

**Comment by ederancz** [comment]
## There are 2 subtasks. 

### A. the recording the photodiode signal via ONIX analogue input.
1kHz sampling rate should be enough (but we should test in action) 

### B. to signal the stimulus parameter. 
In one small square at the bottom of one of the screens via bonvision. 
We need 3 states as follows:
1. Idle (no vis stimulus) - middle grey 
2. Moving stimulus on (both open- and closed-loop modes) - white
3. Halt - black

**Comment by RoboDoig** [comment]
Regarding A) - this should be taken care of by the existing insertion workflow. We can't connect to the same ONIX board on the main workflow while the insertion workflow is running. I think this should already be essentially implemented since the insertion workflow is logging analogue data and is synchronised with HARP.

**Comment by EleonoraAmbrad** [comment]
@RoboDoig you are right, however, as we will not only use Main workflow with Insertion Workflow but also with the photometry setup, we could add an analog IO node in Main as well. We anyway need to create another one for the photometry to implement synchronisation signal (https://github.com/neurogears/vestibular-vr/issues/56).

**Comment by RoboDoig** [comment]
OK I see, so in the photometry version of the experiment, everything is contained in the Main workflow? No second insertion workflow running?

I've made a PR that should produce the desired screen behavior for recording with the photodiode. It should be possible to inspect that this works visually - see PR #62

**Comment by EleonoraAmbrad** [comment]
I tested the workflow, here are some of my remarks:

- I can position the quad in a good place for the photodiode to detect it, so that's good! The quad is mirrored on the neighbouring screen due to the VR mapping, but it shouldn't be a big deal.

- the halts are applied correctly when setting a halt probability >0 in the yml, but the quad does not change colour upon halt. Before TrialLogic start, the quad is grey (as displayed by the bonsai visualiser values). When the TrialLogic starts (using shift + space), the quad turns white. However, when a halt is applied to the VR, the quad does not change colour. This happens in both DrumClosedLoop and in LinearClosedLoop block

- I could not record the signal of the photodiode because there is no analogIN node yet, but I wasn't sure if that's on purpose (when using Main in combination with InsertionWorkflow in the future, I guess we can record the quad signal using the analog node already present in that workflow, as you suggested)

**Comment by RoboDoig** [comment]
Hi @EleonoraAmbrad, thanks for your feedback!

I will look into the colour not changing on halt, if the colour is changing for the other conditions it probably just means I forgot to update the colour switch somewhere in the halt condition, or assigned the wrong colour.

I didn't implement the ONIX stuff in this PR yet, this will be added in the photometry sync PR which I am working on finishing today. For now it can be recorded with a separate workflow if needed.

**Comment by RoboDoig** [comment]
I've updated the PR, the event that updated the halt color was indeed in the wrong place, should be working now!

**Comment by EleonoraAmbrad** [comment]
the quad changes colour as expected! I think it works perfectly well. 

One small comment: because the start of the logging and the start of the trial logic are controlled via two different key down combinations, and can therefore never be precise enough, we will use the change in colour from grey to white to indicate trial logic start and white to grey to indicate trial logic end. I don't think there should be any problem doing this, right?

PS I also did not record the analog signal yet, I wasn't sure if it is implemented in this PR.

**Comment by RoboDoig** [comment]
Closed with #67

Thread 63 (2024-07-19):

### ISSUE TITLE
H2 crash during recording 

### ISSUE THREAD

**Issue by ederancz** [neurogears/vestibular-vr#63]
On every block using the main workflow, H2 seems to crash after ~50 seconds. 
The minimal proportional control workflow does not have this issue. 
Below are a few notes from the logs. 

**H1 logs** for appropriate time (block length) + whenever logging was started and the workflow stopped 
**H2 logs** analogue input (39) and encoder (38) for only ~50 seconds (until the motor stops) 
	but 42 (pulse interval) is logged for the whole block 
	The platform can be rotated after this by hand (i.e. the motor is not clamped). 
	Closed loop visual stimulation keeps running for the block time. 
	There is an error message in the console (see 2 separate examples below). 
```
Not able to parse a Harp Data Frame (03:17:59 PM)!
Raw Harp Data Frame: 03:0C:27:FF:92:29:55:19:00:87:4F:20:4E:04
```
```
Not able to parse a Harp Data Frame (03:23:38 PM)!
Raw Harp Data Frame: 03:0C:27: FF:92:20:4E:8E:02:0C:2A: FF:92:90
```
Note:  Possibly cosmetic, H2 does not show up in console when starting Bonsai. H1 is fine.

**Comment by RoboDoig** [comment]
Just to confirm, is this happening when run from the 'main' branch in the git repo? Or from a different feature branch?
Also is this a full crash (i.e. the whole workflow stops running)?

From the error message it sounds like there is maybe a mistake in one of the HARP messsage filters which causes Bonsai to try and parse a data payload of the wrong type, I will investigate.

**Comment by EleonoraAmbrad** [comment]
we were running the workflow from my branch (Nora-dev). You have a point, I will try to run it from Main branch and see.
No, it's not a full crash, it's more like the rest of the streams are logged and the workflow keeps going, but the motor does not.

**Comment by EleonoraAmbrad** [comment]
I tested the workflow again today using the Main experiment workflow in the screen sync quad branch. I got the same error in the console as mentioned above. After the error, the block logic keeps going, but the VR is not updated. Basically, the block after the DrumClosedLoop will start, but neither the halt protocol nor the flowYtovisualgain are applied. [this is the yml file I used for testing this behavior. ](https://github.com/neurogears/vestibular-vr/blob/nora-dev/src/blockTypesDemo_halt_prob.yml)

**Comment by RoboDoig** [comment]
I haven't been able to reproduce this bug yet as far as I know, at least I don't see those error messages in the console. I think H2/H1 not showing up in the console is cosmetic as they appear to be producing events and receiving commands correctly. Will continue testing on other branches.

**Comment by RoboDoig** [comment]
A couple of initial notes from testing this:

- This error seems to be dependent on the trial logic running, if I run without initiating trial logic I haven't hit this error so far.
- There is a dependence somehow on the length of the block, for example I can reliably produce the same error with an initial block length of 120s and the error appears when the block finishes. A shorter block runtime doesn't produce the same result.

**Comment by RoboDoig** [comment]
OK I think I've found the culprit for this, the basic reason is trying to write commands to the H2 device too fast causing a firmware crash.

The source of this is the `CalculateMotorProcessing` workflow. We are taking separate sources (flow and playback) to drive the motor and using a `CombineLatest` to add them all up to calculate the desired motor movement delta. Because these sources can operate at different sampling rates, sometimes the `CombineLatest` will experience samples from flow and playback in very quick succession. Even if the gain of one of these is at 0 the `CombineLatest` will still fire. In some cases this will cause Bonsai to attempt to write to H2 in short bursts of >1000Hz which can overload the device firmware.

I'll implement a different solution for calculating the motor procession which should fix this, though we do need to test to double check.

Finally, I think the reason the motor can stop even without the error message is that if we crash the firmware there is no guarantee that the H2 device will send us an error - in some cases it may have time to send the response and in others it completely crashes before sending the error message out.

**Comment by RoboDoig** [comment]
Should be fixed by https://github.com/neurogears/vestibular-vr/pull/64, pending testing.

**Comment by RoboDoig** [comment]
Confirmed fixed with testing.

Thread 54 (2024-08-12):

### ISSUE TITLE
Implement file playback as a trial condition.

### ISSUE THREAD

**Issue by RoboDoig** [neurogears/vestibular-vr#54]
One requirement for the trial logic is to have a 'playback' type block where a previously recorded signal (e.g. flow sensor) is replayed on a trial to drive visual flow / motor motion. This is already implemented in the schema and the playback gain can be set along with flow gain etc.

The actual source of this playback signal, however, was not clear at the time of implementing. As a placeholder, the analog input on H2 is used as a playback source in the Bonsai workflow, but this means that the Hall sensor analog input cannot be used.

Following discussions last week, it was decided to rather use a loaded file as the source of playback. This could be, for example, a saved HARP stream .bin file containing values and timestamps of the flow sensor in a previous trial. This introduces the requirement to load a HARP stream file and replay it in Bonsai in real-time with timing as similar to the original signal as possible. There are a few ways of doing this:

1. Use software delays in Bonsai between each timestamped sample to try and replicate the signal.
2. Force the HARP clock on H1 to produce timestamps as fast as possible (e.g. by enabling flow sensor readings) and use those timestamps to implement hardware delays between successive samples in the read .bin file.
3. Use an external hardware timed source for playback, e.g. another HARP device with analog input capabilities.

The most robust option is probably option 2 which we agreed will be the initial implementation.

Another caveat is that although we can replay e.g. flow sensor signals on a trial - because there is some randomness involved in each trial (random delay between run threshold and halt) the visual feedback in a replay trial is not guaranteed to be the same as on the original trial if the replay signal is played back. If an 'exact' replay is required, we would need to log and reload the real delay times for the trial and override the random delay with recorded values.

**Comment by RoboDoig** [comment]
N.B. Another option is to **only** replay visual stimulus on playback trials. This would require logging the frame buffers separately and replaying them as a 'movie'. Also has the challenge of trying to replicate timing on playback trials but might be able to get away with just playing and replaying at a set frame rate.

**Comment by RoboDoig** [comment]
From meeting 6/4/24

Agreed that way forward for playback / open-loop should be based on choosing function generator or matrixreader as playback source.

Means there will be two playback sources, either a function generator with schema defined parameters, or a matrixreader that reads some stored velocity bin file. In addition to just playback gain in the schema therefore, there should be "functionGeneratorGain" and "fileReaderGain".

**Comment by RoboDoig** [comment]
A suggestion from Goncalo, in the fileReader condition we could use the update cycle of the flow sensor as the timing for reading a file.

Simply, each time the optical sensor is read a corresponding value from a file is looked up and sent as the playback signal.

**Comment by ederancz** [comment]
This is part of a new contract. 

If I understand correctly, the idea is that playback will be the same as the open loop, where a matrix reader or function generator provides the command (basically a fake optical flow sensor reading based on a previous recording). Visual stimulus halts will be de-novo generated randomly.  
Regarding how faithful the flow sensor playback is, I am not picky. It could be smoothed and resampled at 200 Hz, and we can disregard any differential jitter of the visual frame presentation. 

This playback should be implemented both for visual stimulus and motor command, so it can be used both at the same time or either of them.  also work not only for the visual stimulus, but the motor command as well.

**Comment by RoboDoig** [comment]
Note to self, can also tie the playback clock to the UpdateFrame node rather than the HARP node.

Ultimately we want an operator that loads a HARP .bin file with the sequnce to playback. It accepts an arbitrary event source (can be HARP or UpdateFrame or a timer) to sample the next value in the sequence.

**Comment by RoboDoig** [comment]
I closed the PR with the initial implementation of this, but I now notice there's an error when using playback as a run gain source, where it tries to access a disposed stream. Investigating now.

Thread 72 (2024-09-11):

### ISSUE TITLE
ExperimentEvents log extra comma in csv

### ISSUE THREAD

**Issue by ikharitonov** [neurogears/vestibular-vr#72]
Found the following line in the ExperimentEvents CSV log file:
`439566.69075200002,Not running, skipping halt`

Not sure where the event descriptions are, could we edit this?

**Comment by RoboDoig** [comment]
Hello, event descriptions are actually currently hard-coded in string operators dotted around the workflow. Simplest solution would be to just remove the comma from this particular string but we could also think of a way to set these in some config file like the schema.

**Comment by ikharitonov** [comment]
I see, thanks for clarifying

**Comment by glopesdev** [comment]
@RoboDoig just one comment for the future, if we wanted to make sure strings are valid we could also make sure we sanitise the descriptions by stripping away all commas before logging.

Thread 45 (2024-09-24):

### ISSUE TITLE
Update to new Bonsai.ONIX interface

### ISSUE THREAD

**Issue by RoboDoig** [neurogears/vestibular-vr#45]
Reminder issue: at some point the workflows should be updated to use the new Bonsai.ONIX interface which is currently under development. This should solve several bugs associated with ONIX being left in an unusable state without reset via oni-repl.exe with the current Bonsai interface.

**Comment by EleonoraAmbrad** [comment]
I will have a meeting with Jon this week to install the new bonsai.ONIX libraries and to set up the new headstage (NP1.0e), as the old headstage (NP1.0) will not be supported anymore. After that, I will make a new Insertion Workflow file so that it can work with the new nodes and headstage.

**Comment by EleonoraAmbrad** [comment]
I created a new insertion workflow using the NP1.0 node and the new "one context" node. However the workflow still crashes after stopping and the only way is to quit and open it again to start the acquisition. This doesn'T happen with very basic workflows that use the new libraries and nodes, so I think it has to do with the insertion workflow specifically, but I can't get my head around it. It seems to have a problem to initialise the ONI node again once the workflow has been stopped.

**Comment by EleonoraAmbrad** [comment]
Update, the insertion workflow with the new libraries and the Main experiment do not work together (I cannot run them in parallel), seems to be the same issue as above?

**Comment by RoboDoig** [comment]
Response from open-ephys regarding the harp clock is that the best solution for this is probably to update to the new ONIX interface. Therefore I'm bumping the priority of this issue as we need to have a stable synchronisation solution.

**Comment by RoboDoig** [comment]
I've updated the main workflow in the `update-onix-interface` branch. Still no sign of the HARP sync input but this may be a wiring issue, need to test when someone is available in the lab.

**Comment by RoboDoig** [comment]
Updated the interface in #78 

Tested today to see if harp sync was now working. We were not getting harp sync messages initially. After talking with open-ephys realised the clock inputs on the board are passive passthrough and there needs to be a direct clock connection to the card.

This still didn't work, but after several attempts and reconfigurations it started working after replugging the clock adapter.

Suggests to me that there is a power issue with the adapter (bad cable, port, power management on the PC), though everything is working now. Need to add something to the visualizer that monitors harp sync events so we don't lose data.

**Comment by RoboDoig** [comment]
Closing as completed with #79

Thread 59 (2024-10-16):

### ISSUE TITLE
Selectable motion clouds

### ISSUE THREAD

**Issue by RoboDoig** [neurogears/vestibular-vr#59]
Motion cloud textures will be selected from a list that is pre-loaded in TextureResources. Right now one must manually select the BindTexture source for the motion clouds. Would be good if the schema allowed named reference to the motion cloud texture selected on each block.

**Comment by ederancz** [comment]
This is part of the new contract.

**Comment by RoboDoig** [comment]
Note for me, check ranson-rig implementation for texture loading

**Comment by RoboDoig** [comment]
A related issue that will fall under this new implementation - currently the workflow assumes a hard-coded number of frames for each motion cloud. This value is used to 'wrap' the motion cloud sequence back around to the start during phase procession. The wrap value should be determined automatically or added as a parameter in the session settings. Ideally automatically.

**Comment by RoboDoig** [comment]
I've implemented the ability to select motion cloud textures by name in the schema and updated the local version of the Bonsai shaders package to allow automatic wrapping see [here](https://github.com/bonsai-rx/bonsai/pull/1999) for longer term support for this feature.

There is still an error on the first motion cloud that is loaded, I think because I've implemented the GetTextureData operator as a source with the texture name as a parameter, somehow the initialisation order means that it tries to access the texture before the name property is updated.

**Comment by RoboDoig** [comment]
@EleonoraAmbrad - please see PR #85 for implementation of this. Seems to work but if you have a chance to test on one of your motion cloud experiments that would be great!

**Comment by EleonoraAmbrad** [comment]
Finally got to test this, here is what I experienced:

- there does not seem to be a correspondance between the cloud displayed on the screen and the cloud that I want to select using the yml file
- the clouds do not seem to change when the time elapses as set in yml file
- the mapping is now limited to 1 screen (might be an artifact from debugging?)

I am also wondering: I will need to disply drifting clouds in open loop experiments, can I implement this using the current workflow? I would need to couple the cloud to the funciton generator producing a sine wave of different frequencies (mimicking temporal frequencies). 

Thank you!

**Comment by EleonoraAmbrad** [comment]
> Finally got to test this, it's working, but I have a few questions:
> 
> * I failed to load a .png file using Add image texture, does the input need to be a .mp4 file? I am asking because I am struggling really hard to generate an .mp4 file with the image size we need, but it seems to be straightforward with .png format so that would make it easier for me to start --> 
update: I managed, it was a matter of not setting number of frames to 1
> * the mapping is now limited to 1 screen (might be an artifact from debugging?)
 update:solved, errpr on my side
> I am also wondering: I will need to display drifting clouds in open loop experiments, can I implement this using the current workflow? I would need to couple the movement of the cloud to a function generator producing a sine wave of different frequencies (mimicking temporal frequencies). Otherwise: will I need to generate the sinewave as csv, similar to what we do for the playback?
> update: just realised that the csv approach might not work because if i produce a sinewave it will not be harp timestamped, so I will probably try to generate a harp timestamped sinewave now
> Thank you!

**Comment by EleonoraAmbrad** [comment]
sf_0=0.01-B_sf=0.06-theta=0-B_theta=0.25-alpha=0-seed=1

When trying to load this .mp4 file, which has the size we need (2 screens = 3840 frame size), I get an error saying: 'Index was outside the bounds of the array'. The error comes from the node BindTexture, within the DoBlock node. I tried changing the index to the one of the image, but it seems that it is automatically loadd (and therefore it cannot be read). 

The file is under Textures, where the others are. Thanks for the help

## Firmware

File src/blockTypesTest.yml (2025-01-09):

%YAML 1.1
---
# yaml-language-server: $schema=schema.json

metadata:
  animalId: plimbo
  rootPath: D:/TrialLogicTestData/
  runGain: 0.0008

motorSettings:
  nominalPulseInterval: 200
  initialPulseInterval: 200
  pulseStepInterval: 2
  pulsePeriod: 10

cameraSettings:
  cameraFrequency1: 100
  cameraFrequency2: 100
  cameraExposure1: 5000
  cameraExposure2: 5000
  cameraGain1: 1
  cameraGain2: 1

blocks: [
  &DrumWithMotion
  {
    alias: DrumWithMotion,
    stimulus: {
      type: "grating",
      offset1: 0,
      offset2: 0,
      extent1: 360,
      extent2: 0
    },
    haltProtocol: {
      minumumDelay: 0.1,
      randomDelay: 1.5,
      haltTime: 2,
      haltGain: 0,
    },
    haltProbability: 1,
    totalRuntime: 40,
    flowYToVisualGain: 1,
    flowYToMotorGain: 0,
    flowYToRunGain: 1
  },
  &DrumWithReversHalt
  {
    alias: DrumWithReverseHalt,
    stimulus: {
      type: "grating",
      offset1: 0,
      offset2: 0,
      extent1: 360,
      extent2: 0
    },
    haltProtocol: {
      minumumDelay: 0.1,
      randomDelay: 1.5,
      haltTime: 2,
      haltGain: 1,
    },
    haltProbability: 1,
    totalRuntime: 240,
    flowYToVisualGain: 1,
    flowYToMotorGain: 0,
    flowYToRunGain: 1,
    initialVisualMovementDelta: 0
  },
  &DrumWithPlaybackCloud
  {
  alias: DrumWithPlaybackCloud,
    stimulus: {
      type: "cloud",
      textureName: test-cloud-2,
      offset1: 0,
      offset2: 0,
      extent1: 360,
      extent2: 0
    },
    haltProtocol: {
      minumumDelay: 0.1,
      randomDelay: 1.5,
      haltTime: 2,
      haltGain: 0,
    },
    playbackFilePath: C:/Users/ONIX/Desktop/_playback.csv,
    haltProbability: 1,
    totalRuntime: 20,
    flowYToVisualGain: 0,
    flowYToMotorGain: 0,
    flowYToRunGain: 0,
    playbackToVisualGain: 1,
    playbackToRunGain: 1,
  },
  &DrumWithPlayback
  {
    alias: DrumWithPlayback,
    stimulus: {
      type: "grating",
      offset1: 0,
      offset2: 0,
      extent1: 360,
      extent2: 0
    },
    haltProtocol: {
      minumumDelay: 0.1,
      randomDelay: 1.5,
      haltTime: 2,
      haltGain: 0,
    },
    playbackFilePath: C:/Users/ONIX/Desktop/_playback.csv,
    haltProbability: 1,
    totalRuntime: 20,
    flowYToVisualGain: 0,
    flowYToMotorGain: 0,
    flowYToRunGain: 0,
    playbackToVisualGain: 1,
    playbackToRunGain: 1,
  },
]

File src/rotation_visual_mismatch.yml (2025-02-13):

%YAML 1.1
---
# yaml-language-server: $schema=schema.json

metadata:
  animalId: plimbo
  rootPath: D:/TrialLogicTestData/
  runGain: 0.0008

motorSettings:
  nominalPulseInterval: 200
  initialPulseInterval: 200
  pulseStepInterval: 2
  pulsePeriod: 10

cameraSettings:
  cameraFrequency1: 60
  cameraFrequency2: 60
  cameraExposure1: 5000
  cameraExposure2: 5000
  cameraGain1: 1
  cameraGain2: 1

blocks: [
  &DrumClosedLoop
  {
    alias: DrumBase,
    playbackFilePath: "C:/Users/ONIX/Desktop/playback_file_b3m3_4.csv",
    stimulus: {
      type: "cloud",
      textureName: training_cloud_1,
      offset1: 0,
      offset2: 0,
      extent1: 360,
      extent2: 0
    },
    haltProtocol: {
      minumumDelay: 0,
      randomDelay: 1.5,
      haltTime: 2,
      haltGain: 0
    },
    totalRuntime: 1,
    flowYToVisualGain: 0,
    flowYToMotorGain: -5000,
    flowYToRunGain: 1,
    playbackToMotorGain: 0,
    flowSmoothing: 20,
    haltProbability: 0
   },
  &DrumClosedLoopReverseHalt
 {
    alias: DrumWithReverseHalt,
    playbackFilePath: "C:/Users/ONIX/Desktop/playback_file_b3m3_4.csv",
    stimulus: {
      type: "cloud",
      textureName: training_cloud_1,
      offset1: 0,
      offset2: 0,
      extent1: 360,
      extent2: 0
    },
    haltProtocol: {
      minumumDelay: 0,
      randomDelay: 0,
      haltTime: 2,
      haltGain: 1,
    },
    haltProbability: 0.4,
    totalRuntime: 1200,
    runThresholdDecay: -0.2,
    flowYToVisualGain: -20,
    flowYToMotorGain: -5000,
    flowYToRunGain: 1,
    playbackToMotorGain: 0,
    flowSmoothing: 20,
    initialVisualMovementDelta: 0
  },
]

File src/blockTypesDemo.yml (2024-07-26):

%YAML 1.1
---
# yaml-language-server: $schema=schema.json

metadata:
  animalId: plimbo
  rootPath: D:/TrialLogicTestData/
  runGain: 0.0008

motorSettings:
  nominalPulseInterval: 200
  initialPulseInterval: 200
  pulseStepInterval: 2
  pulsePeriod: 10

blocks: [
  &LinearPlaybackMismatch
  {
    alias: LinearPlaybackMismatch,
    haltProtocol: {
      minumumDelay: 0.1,
      randomDelay: 0.5,
      haltTime: 2,
      haltGain: 0,
    },
    stimulus: {
      type: grating,
      spatialFrequency: 0.5
    },
    haltProbability: 0.8,
    totalRuntime: 60,
    playbackToVisualGain: 1,
    playbackToRunGain: 1,
    playbackFilePath: "C:/Users/ONIX/source/ae-dev/vestibular-vr/analysis/playback_file.csv"
  },
  &DrumClosedLoop
  {
    alias: DrumBase,
    stimulus: {
      type: "grating",
      offset1: 0,
      offset2: 0,
      extent1: 360,
      extent2: 0
    },
    haltProtocol: {
      minumumDelay: 0.1,
      randomDelay: 1.5,
      haltTime: 2,
      haltGain: 0,
    },
    haltProbability: 1,
    totalRuntime: 20,
    flowYToVisualGain: 0,
    flowYToMotorGain: 5000,
    flowYToRunGain: 1
  },
  &LinearClosedLoopMismatch
  {
    alias: LinearClosedLoopMismatch,
    haltProtocol: {
      minumumDelay: 0.1,
      randomDelay: 0.5,
      haltTime: 2,
      haltGain: 0,
    },
    stimulus: {
      type: grating,
      spatialFrequency: 0.5
    },
    haltProbability: 1,
    totalRuntime: 20,
    flowXToVisualGain: 1,
    flowXToRunGain: 1
  },
  {<<: *LinearPlaybackMismatch},
  {<<: *DrumClosedLoop},
  {<<: *LinearPlaybackMismatch},
  {<<: *LinearClosedLoopMismatch},
  {<<: *DrumClosedLoop},
  {<<: *LinearClosedLoopMismatch},
  {<<: *DrumClosedLoop},
  {<<: *LinearClosedLoopMismatch},
  {<<: *DrumClosedLoop},
  {<<: *LinearClosedLoopMismatch}
]

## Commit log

2022-09-19 \_pcb folder added; first pcb versions & datasheets
    [1st abstract project.kicad_pcb, 1st abstract project.kicad_sch, H1 - Onboard Harp Configuration.kicad_sch, H2 - Harp Motor device.kicad_sch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]
2023-01-17 Timestamped flow and lick sensors
2023-01-17 Camera trigger and configuration
2023-01-17 Test valve toggle
2023-01-17 Test valve pulse
2023-03-07 New folder structure
    [responses.csv, test.csv]
2023-03-14 Initial motor control workflow
2023-08-31 Add camera monitor for manipulator testing
2023-08-31 Avoiding writing motor commands while motor engaged
2023-09-12 Probe visualizer prototype
2023-10-26 create insertion workflow, add neuropixels shader window visualizer
2023-10-27 Add initial logging for insertion workflow
2023-10-30 Completed logging workflow for insertion workflow
2023-10-31 Remove unnecessary planning files, streamline to Bonsai project
    [1st abstract project.kicad_pcb, 1st abstract project.kicad_sch, H1 - Onboard Harp Configuration.kicad_sch, H2 - Harp Motor device.kicad_sch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]
2023-10-31 Prototype schema implementation
2023-10-31 Implement prototype loading of session settings
2023-11-02 Prototype for trial sequence
2023-11-06 Completed full prototype trial logic
2023-12-05 Removing obsolete FilterMessage
2023-12-05 Remove other obsolete FilterMessage
2023-12-05 Remove encoder obsolete FilterMessage
2024-02-13 Fix analog IO bug in main insertion workflow
2024-02-14 Add flow sensor input as movement delta source
2024-02-14 Added prototype motion cloud block to trial logic
2024-02-15 Testing cameras, fixing openTK dependency
2024-02-15 Add camera control logic
2024-04-04 Add basic H2 device logic
2024-04-09 Modifiable visual flow sources
    FlowX, FlowY, rotarty motion and playback source all contribute to phase procession, according to gain set in schema.
2024-04-09 Make rotary motion (flowY) contribute to running threshold
2024-04-09 Initial motor procession calculation
2024-04-09 Creation of motor pulse command
2024-04-09 Add further motor gain channels
2024-04-10 Testing motor control with new schema parameters
2024-04-10 Use CombineLatest for motor procession calculation
2024-04-10 Remove mouse wheel debug
    Dangerous while motor is turned on!
2024-07-02 Add prototype test workflow for screen sync quad logic
2024-07-09 Prototype logic for photometry sync
2024-07-18 Alternate motor signal sampling approach
2024-07-19 Basic playback file conversion script
    [playback_file.csv]
2024-07-19 Basic Bonsai pattern for playback
    [playback_file.csv]
2024-07-19 Prototype playback stream in main workflow
2024-07-26 Add analog frame count logging
2024-08-05 Re-add analog frame logging
2024-09-16 Initialise motor playback with 0
2024-09-16 Add H2 device schema
2024-09-17 Use aeon api for device loading
2024-09-26 Simple notebook for encoder vs. flow sanity check
2024-09-30 Added direct pulses test workflow for calibration
2024-10-16 Fix texture frame initialisation bug
    If a longer texture is initially loaded, followed by a shorter one, BindTexture will initially try and load the last indexed frame which may be out of bounds of the longer texture length. Fix by alwa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
2024-10-16 Example generating a valid sin wave playback file
    [playback_file.csv, sin_playback.csv]
2024-10-31 Implement flow smoothing in main workflow
2024-10-31 Add camera parameters to schema
2024-10-31 Add schema parameters for cameras to main workflow
2024-10-31 Update aeon package and add gain parameters to cameras
2025-02-12 Enable heartbeats in Harp devices
2025-03-06 Add some models and placements
    [box.obj, cone.obj, cricket.obj, cube.obj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]
2025-03-06 Prototype arena
2025-03-11 Add camera acqusition
2025-03-11 Logging of current relevant data streams
